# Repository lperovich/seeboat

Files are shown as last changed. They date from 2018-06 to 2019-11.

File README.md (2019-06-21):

# SeeBoat

Laura Perovich (perovich@media.mit.edu, Object-based Media, MIT Media Lab)

This project includes the code, hardware, and fabrication guides for SeeBoat, a community centered waterbody monitoring and data display platform. 

SeeBoat is a fleet of remote controlled boats that measure and display water quality in real time. It allows communities to explore water quality in their local lakes, rivers, and streams by changing the color of the boat in response to changes to the water quality. This data physicalization contextualizes the information and makes the water pollution data present in people's daily lives.

The boats measure water temperature, conductivity, and turbidity and display the data by real-time changes to the colors of the LEDs on the boat. Numeric sensor data is also transmitted via radio, visible through an Android app, and can be further recording using long exposure photos. SeeBoat makes environmental data experiential and interactive to help both communities and researchers better understand pollution and its implications.

The system is based on the Adafruit Feather M0 with RFM95 LoRa Radio (900MHz).

See "hardware" for a parts list, sensor schematics and board files, and 3D print files for sensors attachments.

See "software" for Arduino code for the entire system (main) and for each of the sensors (testing)

See "tutorials" for sensor fabrication guides and testing recommendations.

With technical contributions from Don Blair, Robert Henning, Sophia Struckman, Rod Bayliss, Rima Rebei, and Talia Spitz. Additional testing and assistance by ECO youth group (GreenRoots), Katherine Paseman, Claudia Chen, and Brian Mayton. 

Thanks to contributors Sara Wylie (Northeastern University) and Roseann Bongiovanni (GreenRoots). 

With funding and support from the Object Based Media (V. Michael Bove), the Media Lab Elements Fellows, and the Council for the Arts at MIT.

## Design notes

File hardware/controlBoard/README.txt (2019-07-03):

Laura Perovich: SeeBoat control board for all the sensors 

--third board layer to be used with Featherwing ultimate GPS and Feather M0 LoRa
--see github parts list in hardware folder for parts details

######### Update 7/3/19
Fixed the labels on the LED strand connector

######### Update 6/23/18
Removed on board LED, spaced out the headers to better fit all the parts and the labels
Included DotStar LED strand connector
Water sensor to tell if it's in water is unnecessary, not implemented

######### Update 5/25/17
Combines the fishet-0.1 board with GPS to works as a breakout board for the feather M0 w/LoRa

parts from the fishnet to include:
*tricolor LED (3 pwm pins, other sides to ground)
*on/off switch for board
*temperature sensor connector (SDA, SCL, GND, PWR)
*turbidity sensor connector
*conductivity sensor connector
*water sensor (to tell if it's in water or not) [UNNECESSARY, NOT IMPLEMENTED]

GPS featherwing includes:
*GPS
*clock via GPS

#############################################
ORIGINAL BOARD LAYOUT:
# Adafruit-Ultimate-GPS-FeatherWing-PCB
PCB files for the Adafruit Ultimate GPS FeatherWing
Format is EagleCAD schematic and board layout
For more details, check out the product page at
   * https://www.adafruit.com/products/3133
Designed by Adafruit Industries.  
Creative Commons Attribution, Share-Alike license, check license.txt for more information
All text above must be included in any redistribution

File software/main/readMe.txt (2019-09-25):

SeeBoatRx goes on the feather that's attached to the computer and receiving the data.

SeeBoatFeather goes on the feather that's on the boat. It needs a breakout board with sensor ports plugged into it. In theory it can also have a GPS featherwing plugged in and keep track of GPS location, but in practice this doesn't seem to work (it never gets a fix).

seeBoatGPSdataSD is a workaround for this GPS issue. It can go on an adafruit feather M0 data logging with SD card board that is plugged into an adafruit GPS with featherwing and an extended antenna and can be added to the SeeBoat to seperately log the position of the boat as it is collecting the data. This GPS information saved on the SD card can later be merged with the sensor data saved as a csv on the computer to determine when the boat was at a particular location and create a digital map of the path of the boat and the data. 

The dataToCSV folder contains python sketches for a variety of computers/versions of python. These can be run while SeeBoat is operating and the SeeBoatRx board is connected to the computer. They will display the data coming in as real time plots and at the same time they will save the received data as a csv on the computer. Always run one of these if you want to keep the data. The data is also time stamped. 

The archive folder contains code no longer in use.

Up one level, the testing folder contains sketches that test each part of the system, including each sensor, to make debugging each part individually easier and allow for greater flexibility in putting the systems together.

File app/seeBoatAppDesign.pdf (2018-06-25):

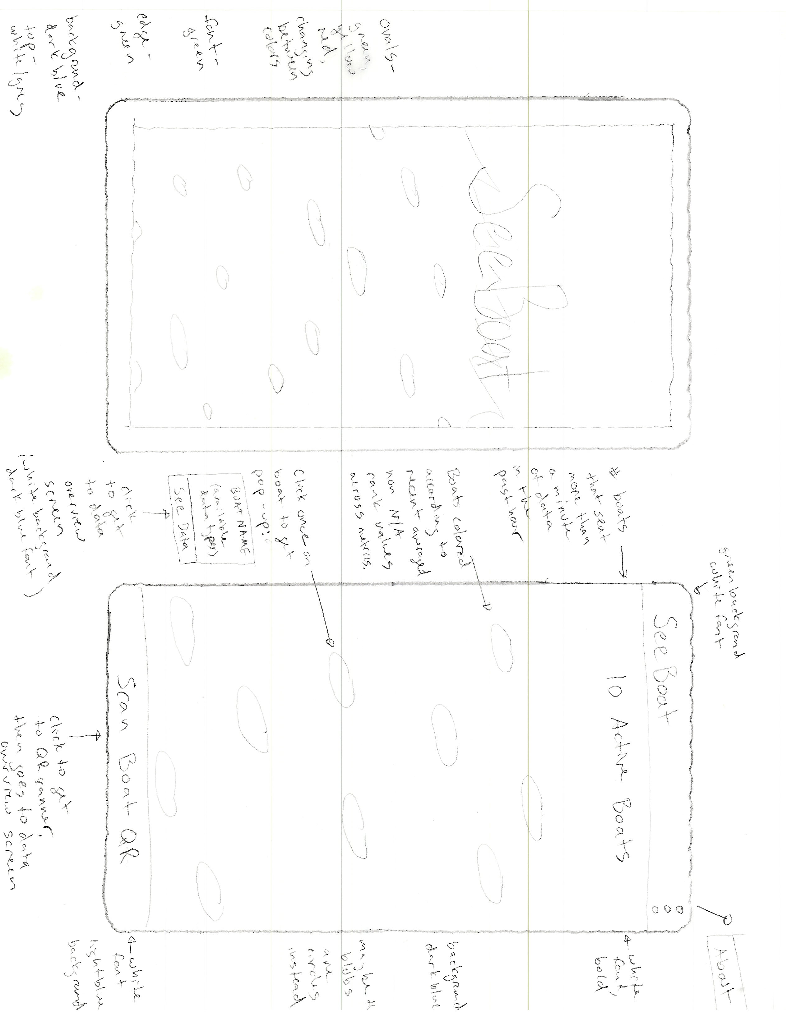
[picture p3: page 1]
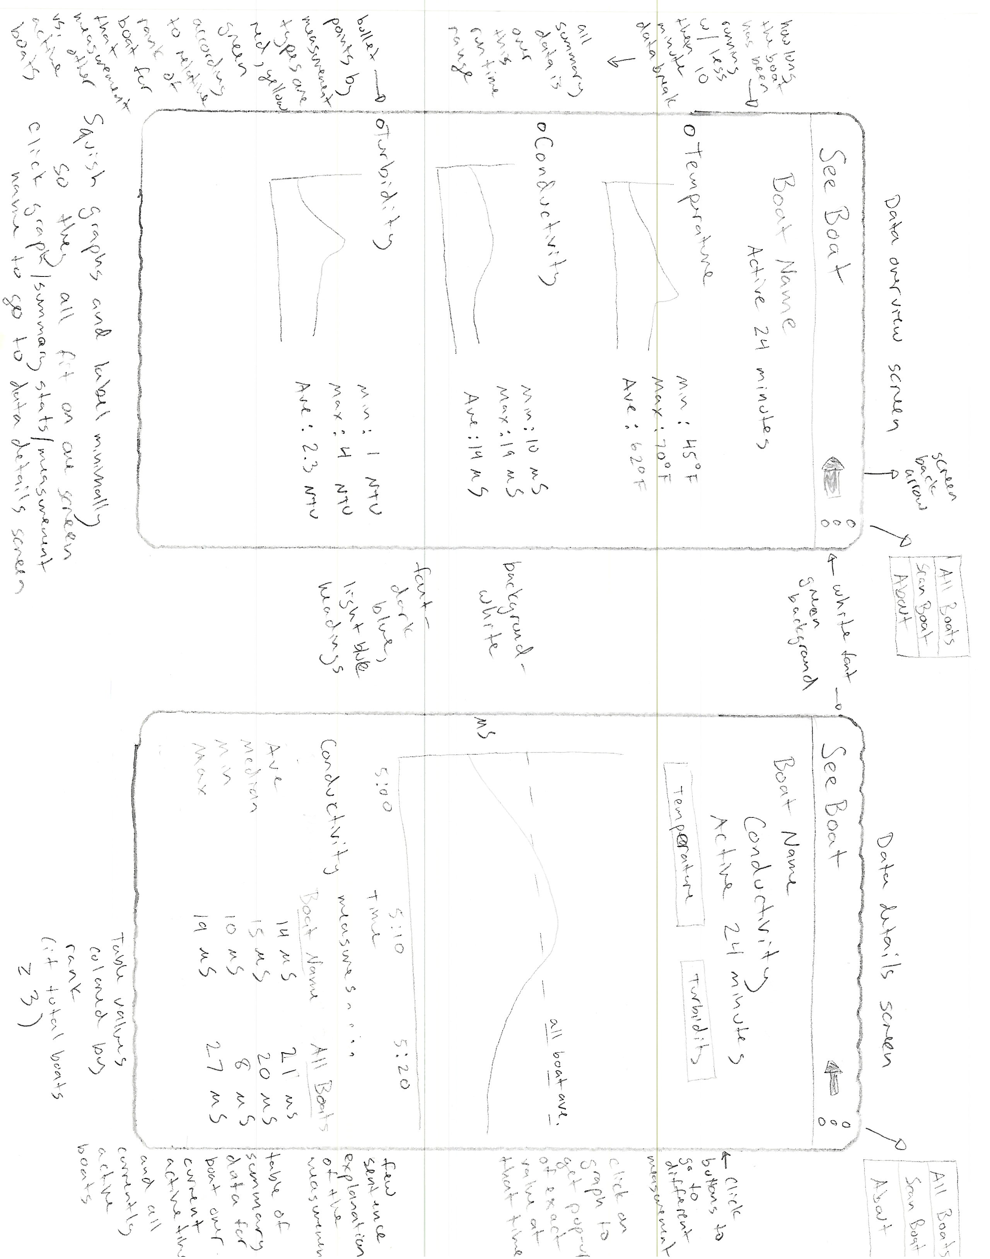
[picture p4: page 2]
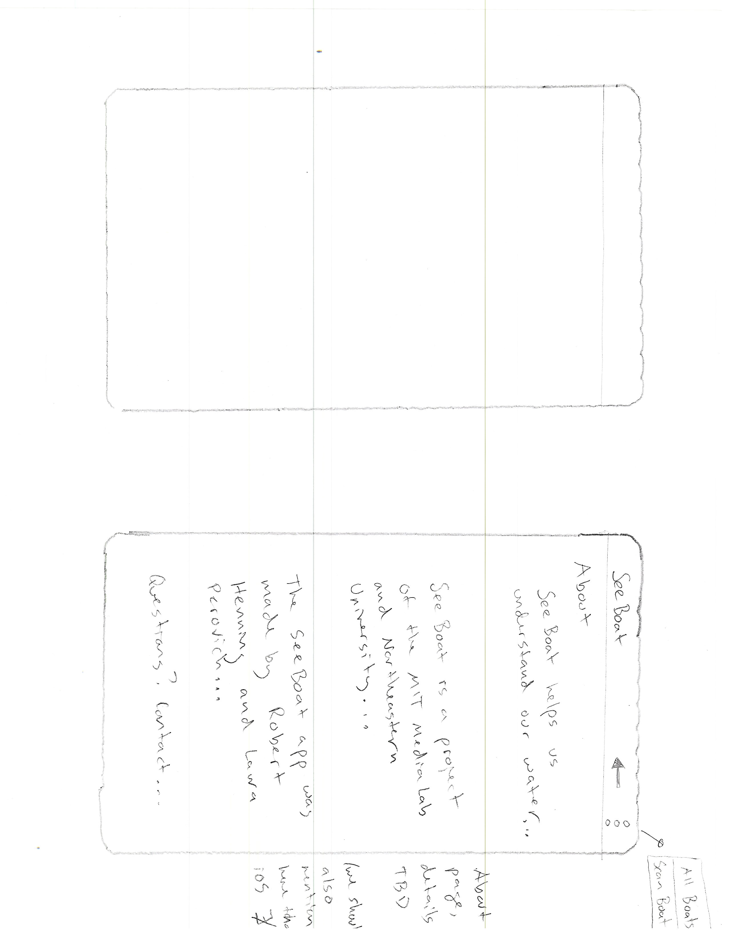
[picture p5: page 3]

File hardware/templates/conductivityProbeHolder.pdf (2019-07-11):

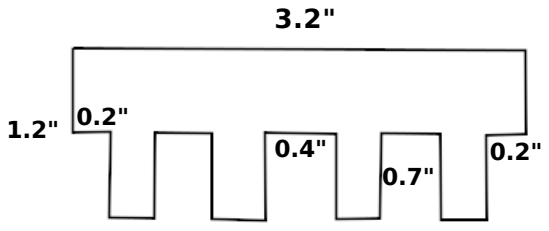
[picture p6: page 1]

1.2"
0.4"
0.7"

0.2"

0.2"

3.2"

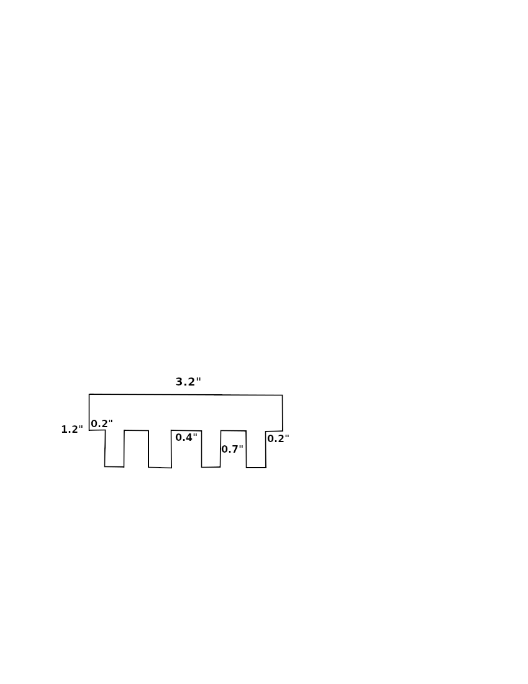
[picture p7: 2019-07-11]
hardware/templates/conductivityProbeHolder.png

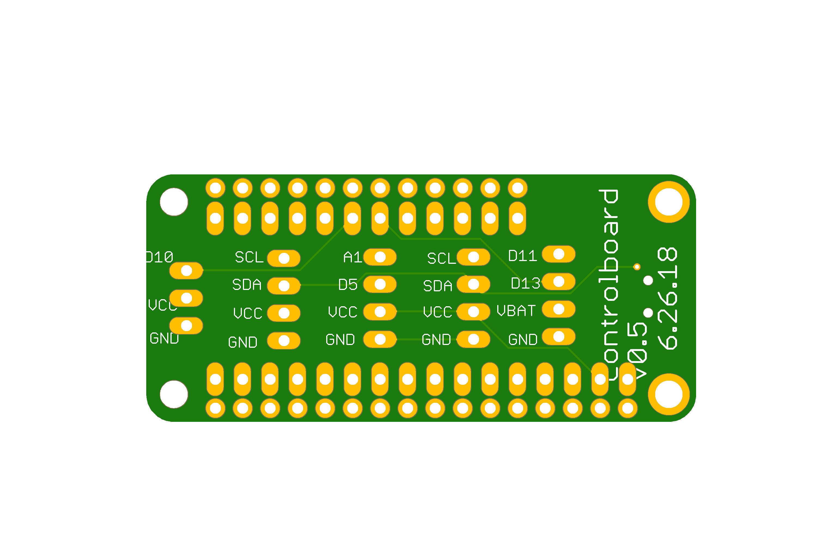
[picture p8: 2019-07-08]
hardware/controlBoard/controlBoard-bottom.png

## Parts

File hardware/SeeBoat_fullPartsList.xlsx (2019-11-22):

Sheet: final
Parts list for SeeBoat & full sensor suite
by Laura Perovich
2018-07-01 | updated June 2019 |  | updated July 2019
BOAT
item |  | part number | place | description | number | cost/item | link
Blackjack 24" Brushless Catamaran RTR |  | PRB08007 | Horizon Hobby | ArtBoat full boat, including radio controller | 1 | $230 | https://www.horizonhobby.com/blackjack-24-inch-catamaran-brushless%3A-rtr-prb08007
LiPo battery Reaction 7.4V 5000mAh 2S 30C LiPo Hardcase: EC3 |  |  | Horizon Hobby | large battery for the boat | 1 | $50 | https://www.horizonhobby.com/74v-5000mah-2s-30c-lipo-hardcase%3A-ec3-dyn9005ec
Krylon K02421007 Fusion for Plastic Spray Paint, Satin Black |  |  | Amazon | to paint the boat so it blends into the background better at night | 1 | $7 | https://www.amazon.com/gp/product/B000C0158E/
isopropyl alcohol |  |  | Amazon | to remove stickers from boat and clean boat | 1 | $8 | https://www.amazon.com/Isopropyl-Alcohol-Solution-16-Ounce/dp/B000P158X8?th=1
AA batteries |  |  | Amazon | for radio controllers | 3 | $15 | https://www.amazon.com/Duracell-MN1500-Duralock-Alkaline-Batteries/dp/B003VSCLMI/
painters tape |  |  | Amazon | to paint the boat so it blends into the background better at night | 1 | $10 | https://www.amazon.com/STIKK-Painters-Release-Finishing-Masking/dp/B01MYP8R5B
600-800 grit sandpaper |  |  | Amazon | to prep the boat for painting | 1 | $7 | https://www.amazon.com/INDUSTRIES-4471-Sandpaper-9-Inch-11-Inch/dp/B001AVYXVU
 |  |  | Amazon
HobbyKing 350w 25A Power Supply (100v~120v) |  |  | Hobby King | liPo battery charger | 1 | $46 | https://hobbyking.com/en_us/hobbyking-350w-25a-power-supply-100v-120v.html
iCharger 208B 350W 8s Balance/Charger |  |  | Hobby King | liPo battery charger | 1 | $126 | https://hobbyking.com/en_us/icharger-206b-300w-8s-balance-charger.html
Stealthwake 23" Brushed Deep-V RTR |  |  | Horizon Hobby | SeeBoat boat, including radio controller, and more space for the sensors than the ArtBoat boat | 1 | $160 | https://www.horizonhobby.com/boats/electric-boats/stealthwake-rtr-23-inch-brushed-deep-v-prb08015
Reaction 7.4V 5000mAh 2S 30C LiPo Hardcase: EC3 |  |  | Horizon Hobby | large battery for the boat, a Ni battery is included with the boat, but this one is better for longer use | 1 | $50 | https://www.horizonhobby.com/74v-5000mah-2s-30c-lipo-hardcase%3A-ec3-dyn9005ec
CONTROL BOARD
item |  | part number | place | description | number | cost/item | link
Adafruit feather M0 LoRa RMF95 900MHz |  |  | Adafruit | main radio board | 1 | $35 | https://www.adafruit.com/product/3178
Adafruit ultimate GPS featherwing |  |  | Adafruit | GPS breakout | 1 | $40 | https://www.adafruit.com/product/3133
lithium coin cell battery |  |  | Adafruit | for GPS featherwing | 1 | $1 | https://www.adafruit.com/product/380
male headers |  |  | Adafruit | for top board | 1 | $3.00 | https://www.adafruit.com/product/392
feather stacking long female headers |  |  | Adafruit | for middle board | 4 | $1.25 | https://www.adafruit.com/product/2830
feather female headers |  |  | Adafruit | for bottom board | 4 | $1.00 | https://www.adafruit.com/product/2886
micro USB cable |  |  | Amazon | cable for programming feather | 1 | $5.59 | https://www.amazon.com/gp/product/B00NH13O7K
liPo battery 2500mAh mAh 3.7V |  |  | Adafruit | substantial enough to work with LED strip (https://learn.adafruit.com/lightship-led-animation-over-wifi/hardware circuit 1) | 1 | $15 | https://www.adafruit.com/product/328
custom breakout board |  |  | OSH Park | connects to all sensors | 1 | $5 | https://github.com/lperovich/seeboat/tree/master/hardware/controlBoard
resistor SMD 0603 2.7K |  | RNCP0603FTD2K74CT-ND | Digikey | for I2C--exact value is important!! | 2 | $0.10 | https://www.digikey.com/products/en?keywords=RNCP0603FTD2K74CT-ND
resistor SMD 0603 100 ohm |  | RNCP0603FTD100RCT-ND | Digikey | for the optional on-board LED | 3 | $0.10 | https://www.digikey.com/product-detail/en/stackpole-electronics-inc/RNCP0603FTD100R/RNCP0603FTD100RCT-ND/2240425
DPDT switch SMD |  | 401-2013-1-ND | Digikey | turns the board on/off | 1 | $1.07 | https://www.digikey.com/product-detail/en/AYZ0202AGRLC/401-2013-1-ND/1640122
optional SMD LED, dotstar 5050 |  | 2343 | Adafruit | can be used for testing on board, same LED as in strip | 1 | $4.50 | https://www.adafruit.com/product/2343
4-pin header female Molex, LLC 0705430003 |  | WM4802-ND | Digikey | connects out to sensors (female, on board) | 4 | $0.94 | https://www.digikey.com/products/en?keywords=WM4802-ND
4-pin header male Molex Connector Corporation 0014562042 |  | WM9131-ND | Digikey | connects out to sensors (male, on wire) | 4 | $1.46 | https://www.digikey.com/products/en?keywords=WM9131-ND
3-pin header female Molex, LLC 0705430002 |  | WM4801-ND | Digikey | connects out the turbidity sensor (female, on board) | 1 | $0.87 | https://www.digikey.com/products/en?keywords=WM4801-ND
3-pin header male Molex Connector Corporation 14-56-2032 |  | WM10647-ND | Digikey | connects out the turbidity sensor (male, on wire) | 1 | $0.99 | https://www.digikey.com/products/en?keywords=WM10647-ND
flat ribbon cable 3M 3302/16 300SF |  | MC16M-100-ND | Digikey | connects out to sensors and lights | 1 | $95.15 | https://www.digikey.com/product-detail/en/3m/3302-16-300SF/MC16M-100-ND/145737 | verify this is the right answer
wire-white single strand | 22 AWG | C2004W-100-ND | Digikey | for short antenna for LoRA radio | 1 | $16 | https://www.digikey.com/product-detail/en/general-cable-carol-brand/C2004A.12.02/C2004W-100-ND/57495
LIGHTS
item |  | part number | place | description | number | cost/item | link
Adafruit DotStar Digital LED Strip - White 60 LED - Per Meter - WHITE |  |  | Adafruit | 5V plays nice with the feather | 1 | $30 | https://www.adafruit.com/product/2240
silicon clear adhesive for water applications |  |  | Tag Hardware | to glue acrylic strips to boat | 1 | $8.00
1/8" satin ice white acrylic strips (~2"x17" per strip, purchase strips as a block) |  |  | Tap Plastics | testing using acrylic (with epoxy casting?) to display lights through holes cut into the boat to replace the dragonskin silcon encased LED strip on the outside of the boat | 1 | $10 | https://www.tapplastics.com/product/plastics/cut_to_size_plastic/satinice_white/655
pH SENSOR
item |  | part number | place | description | number | cost/item | link
Atlas Scientific EZO pH Circuit Part # EZO-pH |  |  | Atlas Scientific | 3.3V plays nice with the feather | 1 | $38 | https://www.atlas-scientific.com/product_pages/circuits/ezo_ph.html
Atlas Scientific ph probe Part # ENV-40-pH |  |  | Atlas Scientific | 3.3V plays nice with the feather | 1 | $72 | https://www.atlas-scientific.com/product_pages/probes/ph_probe.html
Electrically Isolated EZO™ Carrier Board |  |  | Atlas Scientific | 3.3V plays nice with feather | 1 | $40 | https://www.atlas-scientific.com/product_pages/components/single_carrier_iso.html
pH standards; 4, 7, and 10 |  |  | Hach | to calibrate the probe | 1 | $30 | https://www.hach.com/ph-buffer-solution-kit-color-coded-ph-4-01-ph-7-00-and-ph-10-01-500-ml-each/product?id=7640205069
KCl solution |  |  | Hach | for storing the probe in while it's not in use | 1 | $12 | https://www.hach.com/electrolyte-solution-kcl-3m-50ml/product-parameter-reagent?id=7640207762
3/4” 8-32 screws |  |  | Ace Hardware | to attach the holder to the boat | 2 | $0.15
8-32 nuts |  |  | Ace Hardware | to attach the holder to the boat | 2 | $0.08
5/32 rubber washers |  |  | Ace Hardware | to attach the holder to the boat and water seal | 4 | $0.14
Plastic Expansion Routing Clamp, 5/8" ID, 2-7/16" Long |  |  | McMaster Carr | holder to attach the probe to the boat | 1 | $0.55 | https://www.mcmaster.com/8972T11
1/2” inner diameter foam tubing, ~1” length |  |  | McMaster Carr | foam tubing to go around the probe so it securely attaches in the holder | 1 | $0.9 | https://www.mcmaster.com/4339T5
small rubber band/o-ring |  |  |  | to make the foam tubing secure on the pH probe | 1 | $0.14
5/16" inner diameter o-ring, 1/16" thick |  |  |  |  | 2 |  | pill hardware on mass ave
6/16" inner diameter o-ring, 1/8" thick |  |  |  |  | 2 |  | pill hardware on mass ave
foam tape
CONDUCTIVITY SENSOR
item |  | part number | place | description | number | cost/item | link
custom conductivity board |  |  | OSH Park |  | 1 | $7 | https://github.com/lperovich/seeboat/tree/master/hardware/conductivity
resistor 10K, 0603 |  | YAG2122CT-ND | Digikey |  | 4 | $0.17 | https://www.digikey.com/product-detail/en/yageo/AT0603FRE0710KL/YAG2122CT-ND/5139570
resistor, 2.7K, 0603 |  | RNCP0603FTD2K74CT-ND | Digikey |  | 1 | $0.10 | https://www.digikey.com/product-detail/en/stackpole-electronics-inc/RNCP0603FTD2K74/RNCP0603FTD2K74CT-ND/2240457
resistor, 1M, 0603 |  | YAG4498CT-ND | Digikey |  | 1 | $0.34 | https://www.digikey.com/product-detail/en/yageo/RT0603BRD071ML/YAG4498CT-ND/6616654
resistor, 1K, 0603 |  | RNCP0603FTD1K00CT-ND | Digikey |  | 2 | $0.10 | https://www.digikey.com/product-detail/en/stackpole-electronics-inc/RNCP0603FTD1K00/RNCP0603FTD1K00CT-ND/2240445
resistor, 42K, 0603 |  | YAG4556CT-ND | Digikey |  | 1 | $0.34 | https://www.digikey.com/product-detail/en/yageo/RT0603BRD0742K2L/YAG4556CT-ND/6616712
resistor, 1.2K, 0603 |  | 311-2461-1-ND | Digikey |  | 1 | $0.12 | https://www.digikey.com/product-detail/en/yageo/RT0603DRE071K2L/311-2461-1-ND/6128880
capacitor, 0.1 uF, 0603 |  | C1608X8R1H104K080AB | Digikey |  | 1 | $0.32 | https://www.digikey.com/product-detail/en/tdk-corporation/C1608X8R1H104K080AB/445-8818-1-ND/3248223
diode |  | 641-1331-1-ND | Digikey |  | 2 | $0.37 | https://www.digikey.com/products/en?keywords=641-1331-1-ND
rail splitter |  | TLE2426CLPR | Digikey |  | 1 | $1.86 | https://www.digikey.com/product-detail/en/texas-instruments/TLE2426CD/296-6547-5-ND/371934
op-amp |  | JFET, AD8655ARZ-REEL7CT-ND | Digikey |  | 1 | $2.64 | https://www.digikey.com/product-detail/en/analog-devices-inc/AD8655ARZ-REEL7/AD8655ARZ-REEL7CT-ND/3678589
op-amp |  | TLV2374 (TLV2374IDR) |  |  | 1 | $1.81 | https://www.digikey.com/product-detail/en/texas-instruments/TLV2374IDR/296-11967-1-ND/390435
DPDT switch SMD |  | 401-2013-1-ND | Digikey | switches between the two resistor values (high or low conductivity ranges) | 1 | $1.07 | https://www.digikey.com/product-detail/en/AYZ0202AGRLC/401-2013-1-ND/1640122
wire-green single strand | 22 AWG | C2117G-100-ND | Digikey | to connect the board to screws in probe | 1 | $16 | https://www.digikey.com/product-detail/en/general-cable-carol-brand/C2117A.12.06/C2117G-100-ND/16217
wire-white single strand | 22 AWG | C2004W-100-ND | Digikey | to connect the board to screws in probe | 1 | $16 | https://www.digikey.com/product-detail/en/general-cable-carol-brand/C2004A.12.02/C2004W-100-ND/57495
Molex 2 pin header (female) |  | WM4800-ND | Digikey | to connect the probe wires to the board | 1 | $0.84 | https://www.digikey.com/products/en?keywords=%09WM4800-ND
Molex 2 pin header (male) |  | WM24819-ND | Digikey | to connect the probe wires to the board | 1 | $0.78 | https://www.digikey.com/products/en?keywords=WM24819-ND
3D printed probe |  |  | Eden Vero White | sensor probe | 1
foam tubing: Multipurpose Blended Neoprene Foam Tube, 1" OD, 3/4" ID, 10 Feet Long |  |  | McMaster Carr | connects to the boat directly to hold the conductivity probe in place | 1 | $9.21 | https://www.mcmaster.com/2029n13
plastic to plastic epoxy |  |  | Amazon | to glue the foam tubing to the boat, also used for the turbidity holder and the LED panels | 1 | $7.12 | https://www.amazon.com/gp/product/B01IBOK7FE/
Screws, 6-32 1/2” |  |  |  | for within the probe, water contact | 2
nuts |  |  |  | for within the probe, water contact | 2
black epoxy |  | see turbidity sensor | see turbidity sensor | for waterproofing the screws in the probe | see turbidity sensor | see turbidity sensor | see turbidity sensor
Conductivity 2-point Calibration Standard 2-Pack 8oz each 700 uS and 2000 uS |  |  | Amazon | to calibrate the probe | 1 | $17 | https://www.amazon.com/gp/product/B01F2R2EPE/
Conductivity 2-point Calibration Standard 2-Pack 8oz each 100 uS and 3000 uS |  |  | Amazon | to calibrate the probe | 1 | $17 | https://www.amazon.com/gp/product/B01F7L9QD8/
TURBIDITY SENSOR
item |  | part number | place | description | number | cost/item | link
Infrared Diode ("LED") |  | VSMY2850G | Digikey |  | 1 | $1.06 | https://www.digikey.com/product-detail/en/vishay-semiconductor-opto-division/VSMY2850G/VSMY2850GCT-ND/2615293
Light-to-Frequency Sensor |  | TSL237T | Digikey |  | 1 | $5.31 | https://www.digikey.com/product-detail/en/ams/TSL237T/TSL237-TCT-ND/3095287
0.1 µF capacitor |  | C1608X8R1H104K080AB | Digikey |  | 1 | $0.32 | https://www.digikey.com/product-detail/en/tdk-corporation/C1608X8R1H104K080AB/445-8818-1-ND/3248223
200 ohm resistor |  | Yageo RT0603DRD07200RL | Digikey |  | 1 | $0.12 | https://www.digikey.com/product-detail/en/yageo/RT0603DRD07200RL/311-200DCT-ND/1035740
custom light to freq board |  |  | OSH Park |  | 1 | $3 | https://github.com/lperovich/seeboat/tree/master/hardware/turbiditySensor
custom LED board |  |  | OSH Park |  | 1 | $3 | https://github.com/lperovich/seeboat/tree/master/hardware/turbidityLED
wire-black, stranded | 20-22 AWG |  | Digikey | to connect the boards to each other | 1 | $25 | https://www.digikey.com/product-detail/en/alpha-wire/422010-BK005/422010-BK005-ND/3705786
wire-red, stranded | 20-22 AWG |  | Digikey | to connect the boards to each other | 1 | $25 | https://www.digikey.com/product-detail/en/alpha-wire/422010-RD005/422010-RD005-ND/4935160
wire-grey stranded | 20-22 AWG |  | Digikey | to connect the boards to each other | 1 | $25 | https://www.digikey.com/product-detail/en/alpha-wire/422010-SL005/422010-SL005-ND/4935161
~1/8" acrylic black, roughly 2"x5" |  |  | Amazon | to mount senor & LED at right angles; also to "focus" the LED light | 1 | $13 | https://www.amazon.com/Source-One-LLC-Acrylic-Plexiglass/dp/B06XNXHKQN/
black thermally conductive epoxy |  |  | Amazon | for waterproofing the electronics, as with temperature sensor | 1 | $43.95 | https://www.amazon.com/MG-Chemicals-Thermally-Conductive-Encapsulating/dp/B008UH4CRM
cutting oil; soluble oil |  |  | Amazon | to calibrate the turbidity sensor | 1 | $15 | https://www.amazon.com/CRC-SL2512-Soluble-Oil-32/dp/B000M8O010/
small glass viles |  |  | Discount Vials | to calibrate the turbidity sensor | 1 | $17 | https://www.discountvials.com/6-dram-glass-vial-w-cap/
Hach turbidity standard, 500 mL (Wijnen) |  |  | Hach | THIS IS SUPER TOXIC; to calibrate the turbidity sensor | 1 | $80 | http://www.hach.com/formazin-turbidity-standard-4000-ntu-500-ml/product?id=7640455437
TEMPERATURE SENSOR
item |  | part number | place | description | number | cost/item | link
custom temp board |  |  | OSH Park | custom temperature board | 1 | $5 | https://github.com/lperovich/seeboat/tree/master/hardware/temperatureSensor
digital temperature sensor |  | AT30TS750A-SS8M-T | Digikey | temperature sensor | 1 | $0.60 | https://www.digikey.com/product-detail/en/microchip-technology/AT30TS750A-SS8M-T/1611-AT30TS750A-SS8M-TCT-ND/6831450
resistor, 10K, 1206 |  | RC1206FR-0710KL | Digikey | check this value | 1 | $0.10 | http://www.digikey.com/product-detail/en/RC1206FR-0710KL/311-10.0KFRCT-ND/731430
capacitor, 0.1 uF, 1206 |  | 478-5724-1-ND | Digikey |  | 1 | $0.36 | https://www.digikey.com/product-detail/en/avx-corporation/1206VC104KAT2A/478-5724-1-ND/2136332
flat ribbon cable 3M 3302/16 300SF |  | see control board | see control board | board to control board connector | see control board | see control board | see control board
black epoxy |  | see turbidity sensor | see turbidity sensor | for waterproofing the electronics | see turbidity sensor | see turbidity sensor | see turbidity sensor

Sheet: scrap
BOAT AESTHETICS
LED strip trying to get it more diffuse but still bright enough |  |  |  |  | The plastic appears similar to the translucent or 'opal' acrylic sold for signs and lightboxes. The back face is covered with an adhesive aluminum foil reflector. Aluminum foil tape is available at most hardware stores.
trying to get this effect: https://www.adafruit.com/product/1621
opal acrylic
acrylic and more |  | https://www.piedmontplastics.com/applications/light-boxes | reached out to them via online form 6/6/18 | they will send me some samples, suggested #7328 white
diffuser acrylic sheets |  | http://www.chinaacrylicsheet.com/ | reached out to them via online form 6/6/18 about their backlit diffuser things
more acrylic options |  | https://www.tapplastics.com/ | reached out to them via online form 6/6/18 about their backlit diffuser things | suggested satin ice white--ordered a sample | https://www.tapplastics.com/product/plastics/cut_to_size_plastic/satinice_white/655
more plastics options |  | http://www.eplastics.com/ | reached out to them via email 6/6/18 | suggested this one: http://www.eplastics.com/Plastic/lighting-diffusers/lumen-xt-lw3-polycarbonate-sheet asked for sample
more lightbox focus |  | https://www.lightboxes.com/ | reached out to them via online form 6/6/18 | they suggested an option, I asked if I could get a sample of it 6/8/18 | they wanted to charge $30 to ship the sample, so no go
 |  | http://www.plasticsheets.com/opal-acrylic-sheet/ | has the right material, but UK site
 |  | https://www.cutplasticsheeting.co.uk/frosted-acrylic-perspex-sheeting/opal-frost-acrylic-sheeting | another UK site
 |  | https://www.simplyplastics.com/catalog/products-by-use/plastic-lighting-materials/opal-acrylic-light-diffusing-sheet/c-24/c-110/p-667 | more UK sites
 |  | https://www.cloudynights.com/topic/496450-looking-for-opaque-plastic-for-light-box/ | useful thread!!!
 |  |  | translucent white acrylic from McMaster plus sanding
 |  |  | ask local industrial plastics supplier
acrylic sheets |  | http://www.estreetplastics.com/SearchResults.asp?Search=1%2F8%22+2447&Search.x=0&Search.y=0 | 1/8" 2447 White Translucent Sheet | emailed them about this product
Paint or stickers for boat??
SCRAP
wire-red single strand | 22 AWG |  |  | 1 | 16 | https://www.digikey.com/product-detail/en/general-cable-carol-brand/C2004A.12.03/C2004R-100-ND/53789
wire-black single strand | 22 AWG |  |  | 1 | 16 | https://www.digikey.com/product-detail/en/general-cable-carol-brand/C2004A.12.01/C2004B-100-ND/57431
short male headers |  | Adafruit | for top board | 4 | $0.50 | https://www.adafruit.com/product/3002
short female headers |  | Adafruit |  | 4 | $1.50 | https://www.adafruit.com/product/2940
dragon skin 30 |  | Amazon | for opaque LED strip | 1 | $31 | https://www.amazon.com/dp/B00EOA0EC6/ref=cm_sw_r_cp_api_xzDjAbNHV1FRW
powdered sugar |  | grocery store | to make the LEDs diffuse more through the silicon | 1 | $8 | https://www.amazon.com/Domino-Powdered-Confectioners-Sugar-16oz/dp/B0019N2EQU
waterproof adhesive |  | Amazon | for sealing the holes the LED wires go through and attaching LEDs to boat; other options could work | 1 | $27 | https://www.amazon.com/gp/product/B000H83M4G/
acrylic (1/8", 12"x24") |  | Amazon | for making a box to use for casting the LEDs in silicon | 1 | $25 | https://www.amazon.com/Source-One-LLC-Acrylic-Plexiglass/dp/B01FEF0VQI/
white polyester transparent fabric |  | local fabric store | to put in silicon to diffuse the LED strip more | 1 | $5
aluminum tape for reflecting |  | Amazon | backing for LED strip to maximize light out--test this | 1 | $10 | https://www.amazon.com/Aluminum-Tape-Foil-Ducts-Insulation/dp/B01FROBUXE/

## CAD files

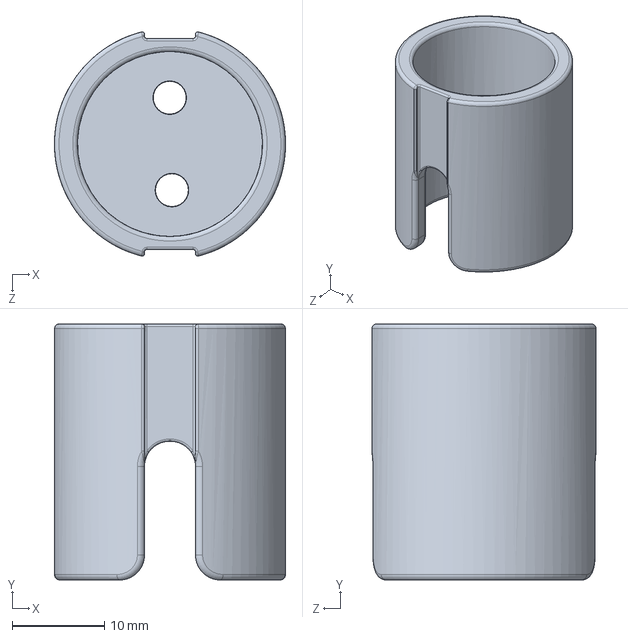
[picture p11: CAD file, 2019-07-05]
hardware/3Dprint/conductivityProbe.SLDPRT
25.0 x 27.7 x 24.2 mm

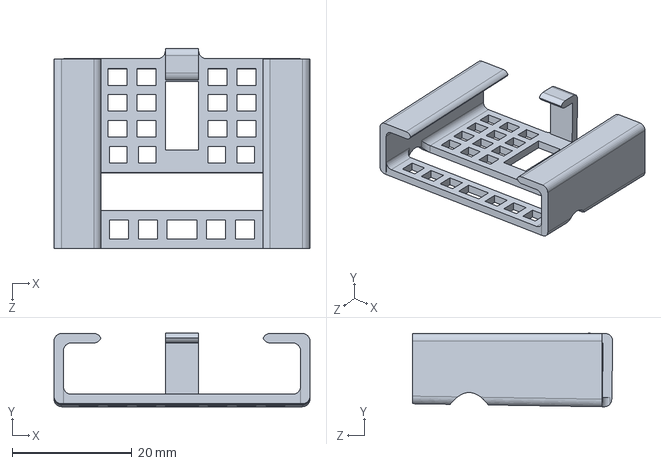
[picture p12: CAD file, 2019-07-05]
hardware/3Dprint/turbidityBoatAttachment.sldprt
42.8 x 12.3 x 33.5 mm

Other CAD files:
hardware/3Dprint/conductivityProbe.DXF
hardware/3Dprint/conductivityProbe.STL
hardware/3Dprint/turbidityBoatAttachment.DXF
hardware/3Dprint/turbidityBoatAttachment.STL

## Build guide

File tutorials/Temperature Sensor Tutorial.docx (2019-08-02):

# Temperature Sensor Tutorial/troubleshooting

Talia Spitz Spring 2019

# Probe

The probe for the temperature sensor is covered in epoxy in order to waterproof it. It is the only part of the sensor which should be immersed in water.

## Manufacturing

### Parts list for the probe:

Part | Amount | Notes | Image

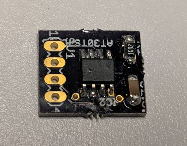
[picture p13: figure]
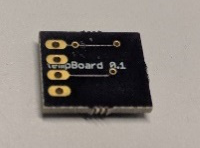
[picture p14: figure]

Custom temp board | 1 | you can find the board schematic at: https://www.dropbox.com/sh/mgy3ndqnzldy1xk/AABXH-txk6h3GChvCx_p5i7ma?dl=0

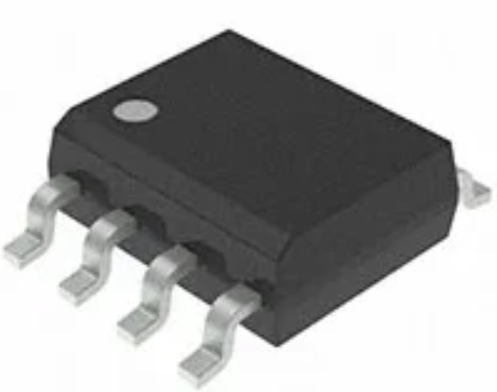
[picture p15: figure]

Digital temp sensor | 1 | Part number: AT30TS750A-SS8M-T, Digikey
10 kΩ resistor, 1206 | 1 | Part number: RC1206FR-0710KL, Digikey
0.1 µF capacitor, 1206 | 1 | Part number: 478-5724-1-ND or 399-4674-1-ND, Digikey

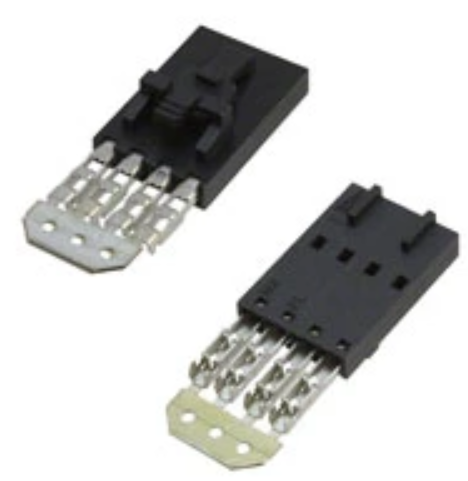
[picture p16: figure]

4-pin header | 1 | Part number: WM9131-ND, Digikey
Wire | 4 (different colors) | By convention, we use black, white, grey, and purple ribbon wire.

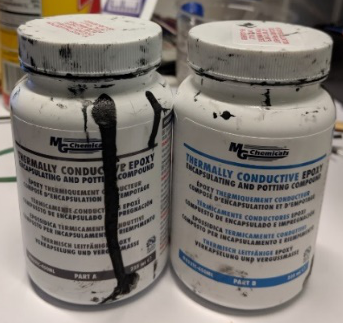
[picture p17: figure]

MG Chemicals epoxy | 1 | Part number: 832TC-450ML https://www.amazon.com/MG-Chemicals-Thermally-Conductive-Encapsulating/dp/B008UH4CRM#product-description-iframe

### Steps:

1) Firstly, you’ll want to attach the wires to the connector. Cut the ribbon wire to about 1 foot in length. Crimp them in place by hand first, then solder them in. When you’re done, carefully push them into the plastic case, and snap off the metal tag. It’s easy to break the wires while you’re doing this, so be gentle. If it’s needed, you can carefully use a pair of pliers to push the wires in.

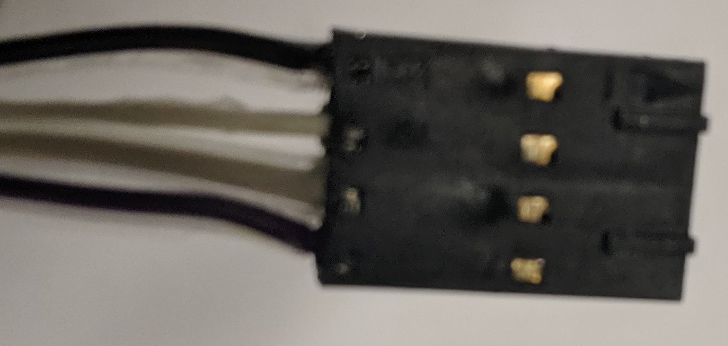
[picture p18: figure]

The finished connection.

2) Follow the board schematic and solder on the resistor, capacitor, and temperature sensor.

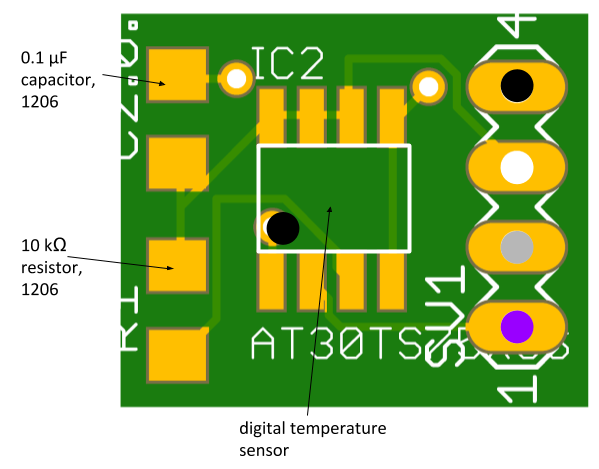
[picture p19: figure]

Annotated temperature circuit board schematic.

3) Solder the wires to their corresponding pins.
4) **Test to see if the sensor works before epoxying it!!** Follow the directions on the epoxy containers to waterproof the probe. The epoxy should cover the whole circuit board and up the wires a little bit.

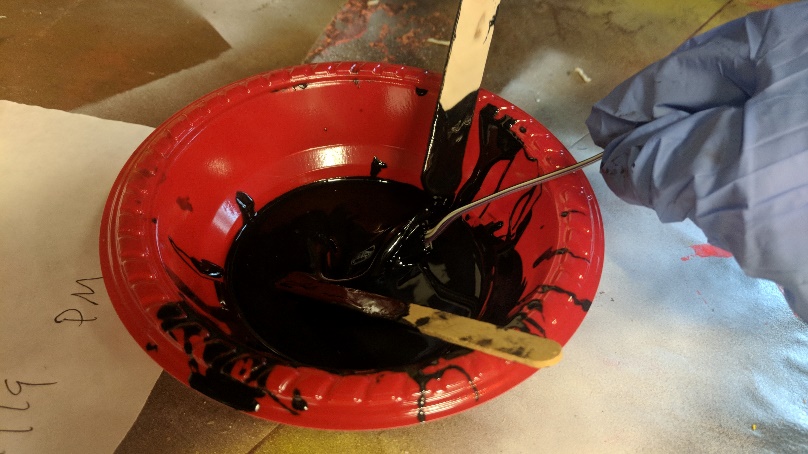
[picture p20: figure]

First dip the board into the epoxy, then use a popsicle stick to spread the epoxy up the wires and make sure the entire board is coated. Once you’re sure it’s covered, gently scrape off excess epoxy so it doesn’t drip while it cures.

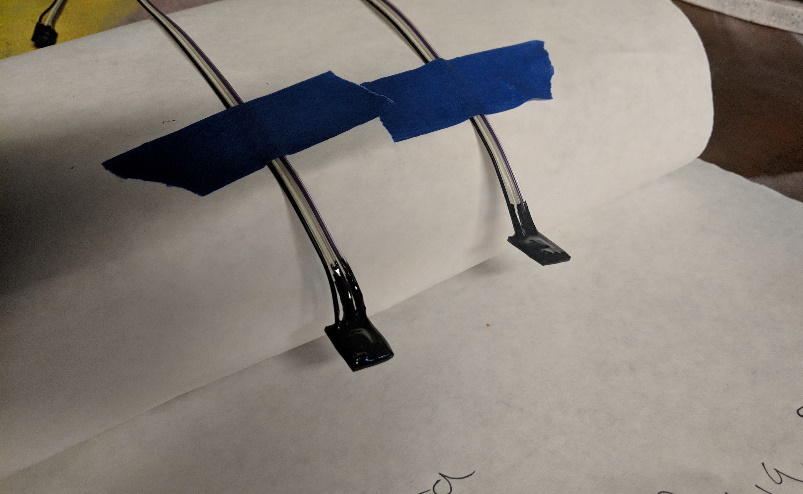
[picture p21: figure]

Leave the epoxied sensors to cure for 24 hours. Check them after a couple of hours to see if you need to touch up any areas with more epoxy, or if you need to scrape off any more excess.

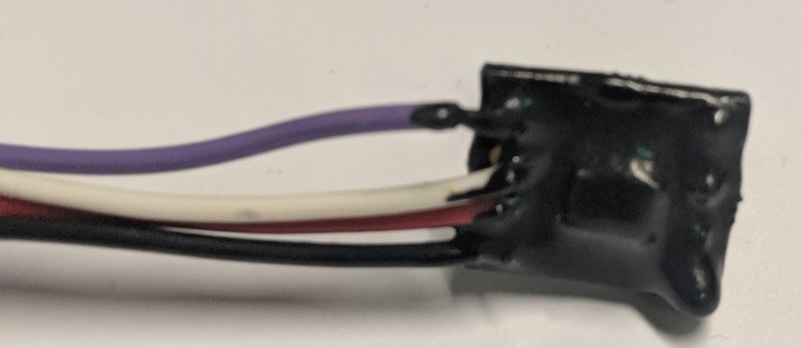
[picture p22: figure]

The cured epoxy (black) should look like this.

# troubleshooting

To test if your temperature sensor is working, plug it into the Feather, and run the ‘tempWire’ (found at: “GitHub\seeboat\software\testing\temperature\tempWire\tempWire.ino”) file in Arduino. The serial monitor should print the temperature reading in both Celsius and Fahrenheit.

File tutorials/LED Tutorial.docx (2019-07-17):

# LED tutorial

# Manufacturing

### Parts list:

Part | Amount | Notes | Image

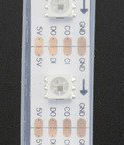
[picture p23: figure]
Adafruit DotStar Digital LED Strip - White 60 LED - Per Meter - WHITE

Adafruit DotStar Digital LED strip | 1 | https://www.adafruit.com/product/2240?length=1

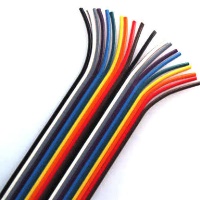
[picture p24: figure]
Image result for ribbon wire

Ribbon wire | ~3 ft | We used black, grey, white, and purple wires.

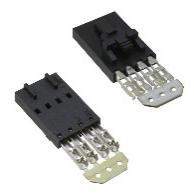
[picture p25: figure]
Image result for WM9131-ND

4-pin header | 1 | Part number: WM9131-ND

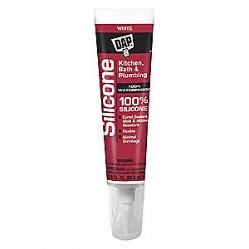
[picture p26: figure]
White Sealant, Silicone, 2.8 oz.

Silicone glue | 1 | https://www.grainger.com/product/406W20?gclid=CjwKCAjwvJvpBRAtEiwAjLuRPZ_Sl7sjaj8k1NH8XQdIhp3zyGGysJu4nPp_T-i7-aUdAsLFmiFH5xoCrLIQAvD_BwE&cm_mmc=PPC:+Google+PLA&ef_id=CjwKCAjwvJvpBRAtEiwAjLuRPZ_Sl7sjaj8k1NH8XQdIhp3zyGGysJu4nPp_T-i7-aUdAsLFmiFH5xoCrLIQAvD_BwE:G:s&s_kwcid=AL!2966!3!281733020561!!!g!427397951721! (https://www.grainger.com/product/406W20?cm_mmc=PPC:+Google+PLA&s_kwcid=AL!2966!3!281733020561!!!g!427397951721!)

### Steps:

1) Measure and cut the LED strand and ribbon wire to the correct lengths based on the drawing below. Every time you cut the strand, you’ll lose one LED, so be careful when measuring.

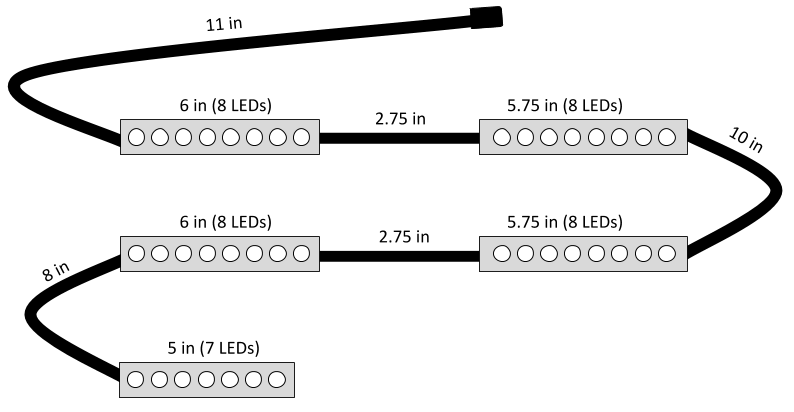
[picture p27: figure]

These are the measurements we used to make the LED strand one continuous piece. The black lines represent the ribbon wire. The 6 in LED strips are for the back side panels, the 5.75 in strips are for the front side panels, and the 5 in strip is for the top panel.

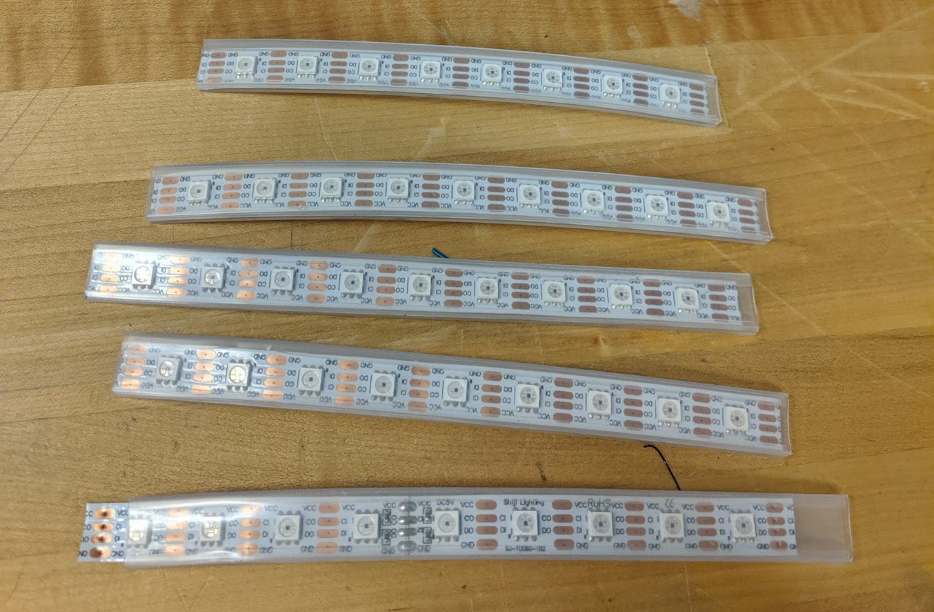
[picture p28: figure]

This is what the strands should look like after they’ve been cut.

2) Use a tack or other wire to make the holes in the LED strip larger so it will be easier to solder.

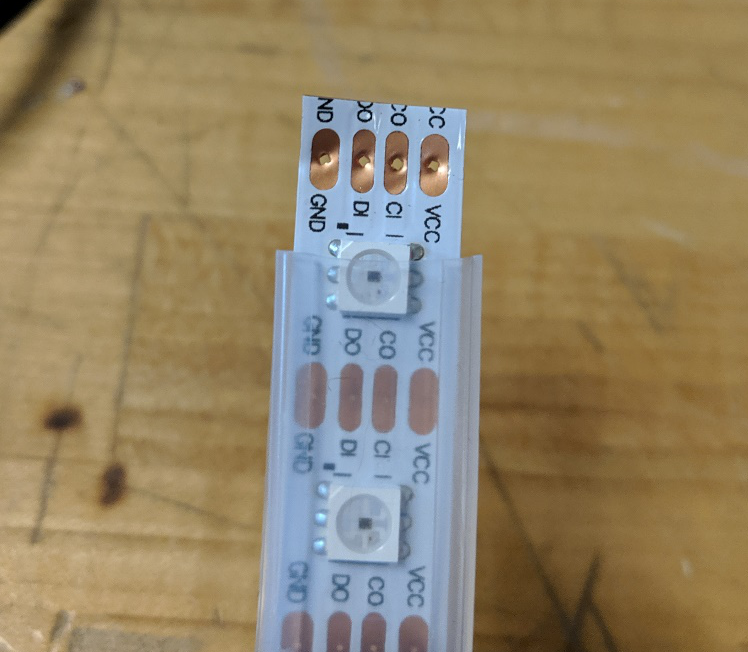
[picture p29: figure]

The top holes were enlarged by poking a wire through them.

3) Strip the ribbon wire, and insert the wires into the holes on the LED strip, and bend them so they stay still while you’re soldering. Try to follow the convention of black wire → GND. Also make sure to trim any free wire after you’re finished soldering.

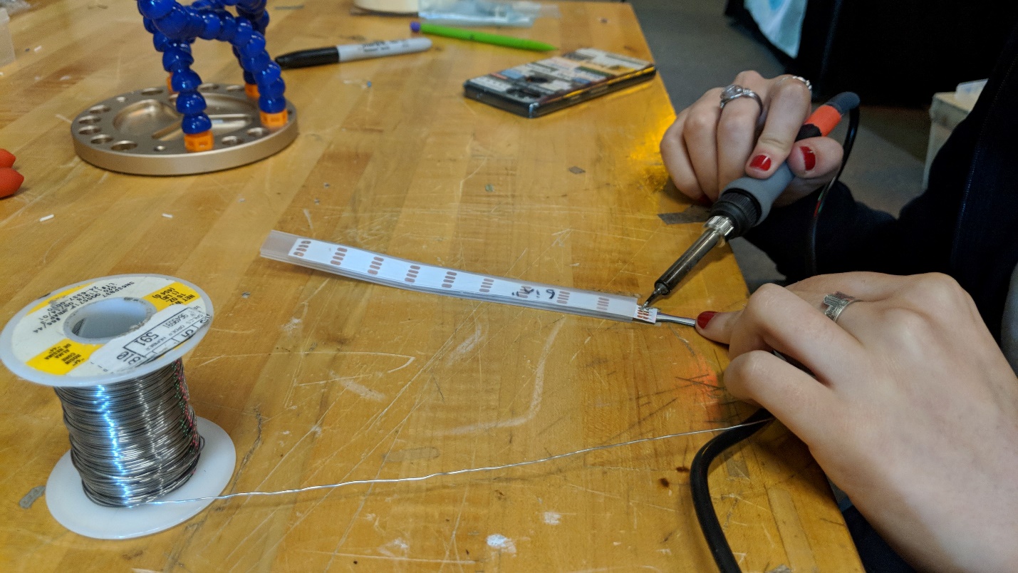
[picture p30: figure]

The wires are threaded through the top of the holes, then bent at the back so it’s easier to solder on the bottom. You can also solder on the top if wire is exposed.

4) Once everything is soldered together, double check that you’ve wired it correctly! If you accidentally switch VCC and GND, you can burn out the LEDs.
5) Test the strip!
6) After you’ve tested the strip, use silicone glue and seal the ends to make it watertight.

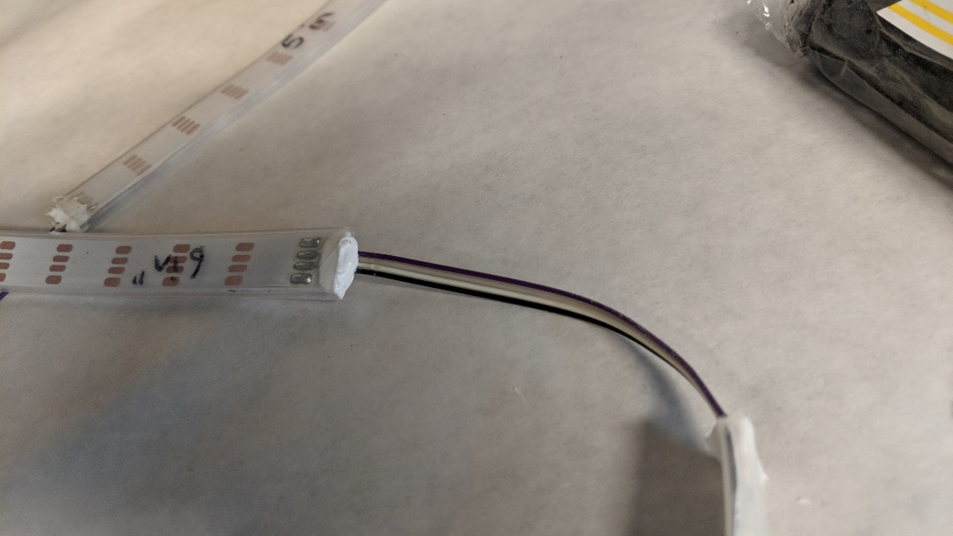
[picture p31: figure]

A sealed LED strip.

# Testing

Use the tester code which can be found at: “GitHub\seeboat\software\testing\LED." The LEDs should cycle through colors all the way down to the end of the strand. If it’s not working, add more solder, and make sure a battery is plugged into the Feather, as sometimes the LEDs are fussy and only work when you plug in a battery.

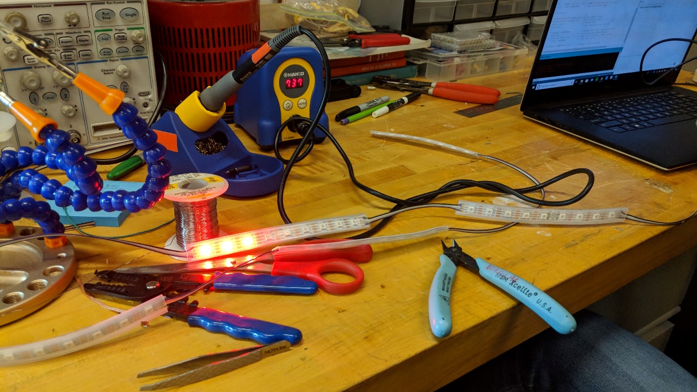
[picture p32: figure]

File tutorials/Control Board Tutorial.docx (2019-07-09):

# Control board Tutorial

# control board parts and schematics

### Parts list for the board:

Part | Amount | Notes
Custom control board | 1 | Can be found in the GitHub at: "GitHub\seeboat\hardware\controlBoard\controlBoard-0.5.brd"
2.7 kΩ resistor, 0603 | 2 | Part number: RNCP0603FTD2K74CT-ND, https://www.digikey.com/products/en?keywords=RNCP0603FTD2K74CT-ND
DPDT switch | 1 | Part number: 401-2013-1-ND, https://www.digikey.com/product-detail/en/AYZ0202AGRLC/401-2013-1-ND/1640122
4-pin header female | 4 | Part number: WM4802-ND, https://www.digikey.com/products/en?keywords=WM4802-ND
3-pin header female | 1 | Part number: WM4801-ND, https://www.digikey.com/products/en?keywords=WM4801-ND
Male headers | 1 | Break to correct size: https://www.adafruit.com/product/392

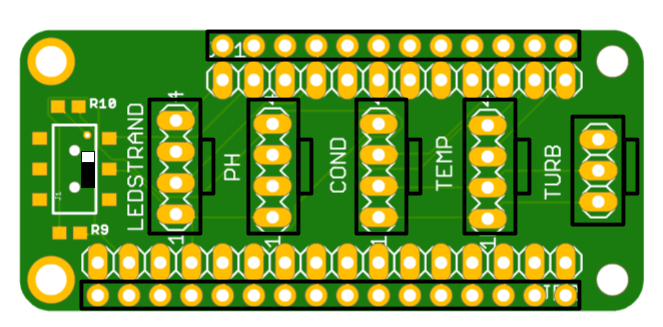
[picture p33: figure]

The schematic above details where each of the parts should go.

# Steps:

1. Solder on resistors, then the switch. Make sure the switch is oriented according to the schematic.
2. Solder on the 4-pin headers and the 3-pin, oriented in the right direction. It’s helpful to just solder one pin, then make sure the header is perpendicular to the board, and then solder the rest.
3. Solder on the male pin legs in the outer holes of the board. It’s helpful to use the female pin counterparts already soldered on a different board to help align the pins correctly. Insert the male pins into the other board, then set the control board on top and solder the pins.
4. All done!

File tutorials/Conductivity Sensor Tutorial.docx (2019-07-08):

# Conductivity Sensor Tutorial/troubleshooting

# Probe

The probe for the conductivity sensor is 3-D printed out of ______. It is the only part of the sensor which should be immersed in water.

## Manufacturing

### Parts list for the probe:

Part | Amount | Notes | Image

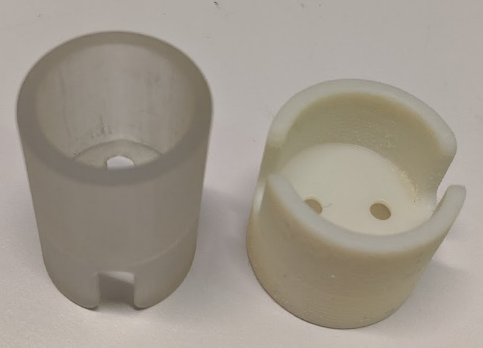
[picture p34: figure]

3D printed probe | 1 | stl file for 3D printing can be found in the Dropbox at: "SeeBoat\Talia\Conductivity\Hardware\probe 2.0.STL"
Single-core wire | 2 | Any single core wire should work, a relatively thin one will be easier to attach.

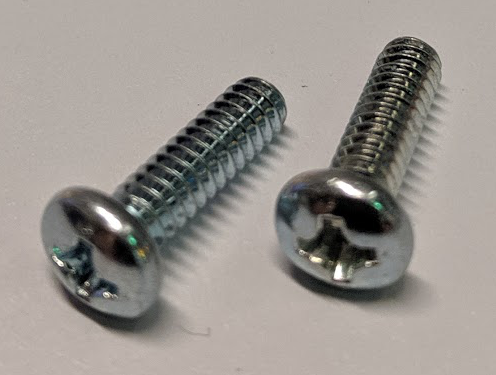
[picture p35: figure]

6-32 ½” screws | 2 | These screws fit the holes in the probe CAD snugly, so they will be the easiest to install.

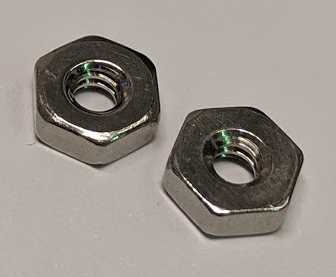
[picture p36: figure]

6-32 ½” nuts | 2 | These are the corresponding nuts.

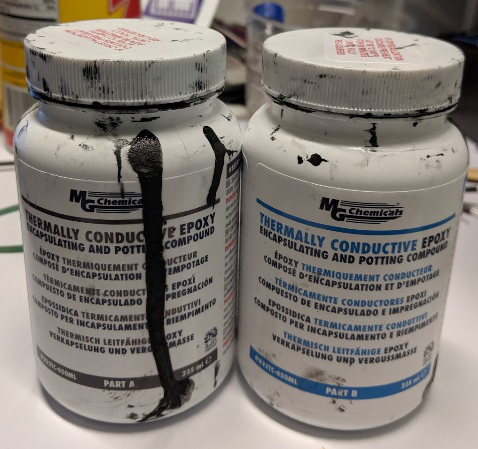
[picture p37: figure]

MG Chemicals epoxy | 1 | Part number: 832TC-450ML https://www.amazon.com/MG-Chemicals-Thermally-Conductive-Encapsulating/dp/B008UH4CRM#product-description-iframe

### Steps:

1) 3D-print the probe using the stl file in the Dropbox folder mentioned above.
2) Gather other materials according to the parts list.
3) Tighten the screws in place, using the nuts. Do not tighten all the way yet.

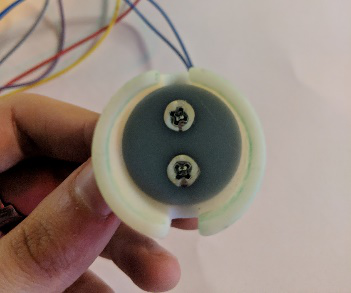
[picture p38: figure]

The head of the screws should be facing as shown above.

4) Carefully wrap exposed wire around each end of the screw, then tighten the nuts on all the way so that the wire is securely clamped down by the nuts.
5) Follow the directions on the epoxy containers to waterproof the probe. The epoxy should cover the threads of the screws and up the wires a little bit.

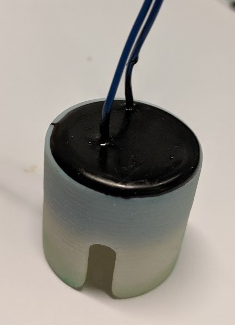
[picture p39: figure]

The cured epoxy (black) should look like this.

6) Connect the ends of the wires to the appropriate pin on the circuit board.

# Circuit Board

The circuit board has a lot of small parts and assembling requires a good amount of patience. Take your time!

## Manufacturing

### Parts list for the circuit board:

Symbol | Value | Part # (if applicable)
R1, R2, R3, R4 | 10 kΩ | YAG2122CT-ND, 0603
R5 | 1 MΩ | YAG4498CT-ND, 0603
R6, R7 | 1 kΩ | RNCP0603FTD1K00CT-ND, 0603
R8 | 47 kΩ | 0603
R9 | 4.7 kΩ | 0603
R10 | 1.2 kΩ | 0603
C2 | 0.1 µF | C1608X8R1H104K080AB, 0603
D1, D2 | N/A | S1BBFDICTND
U1 | N/A | TLV2374IDR
U2 | N/A | TLE2426CLPR
IC1 | N/A | AD8655ARZ-REEL7CT-ND
S1 | N/A | 401-2013-1-ND
-- | N/A | custom circuit board
Header | N/A | WM9131-ND

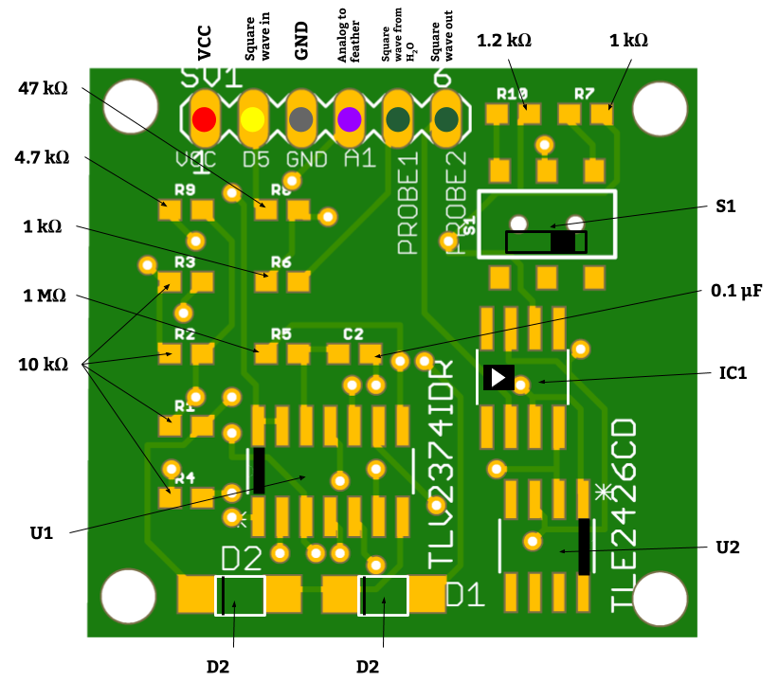
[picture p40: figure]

### Steps:

1) Collect all the parts you need to solder on a print-out of the above schematic (located in the Dropbox at: “SeeBoat\Talia\Conductivity\Hardware\Conductivity Board Diagram.docx”). It helps to tape them to their corresponding labels so you don’t mix them up.
2) Solder each part onto the board.

NOTE: Some of the parts have directionality to them, so make sure you have them oriented the right way. Also, it helps to start adding parts from the middle and then work your way to the edges.

3) Solder the wires which connect to the Feather into header. The order in which you solder them is very important, so be sure to double check they match:

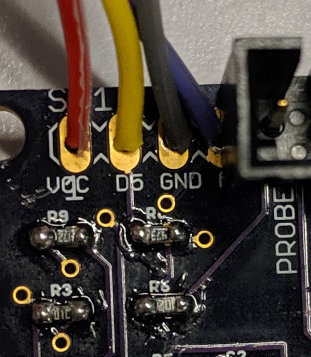
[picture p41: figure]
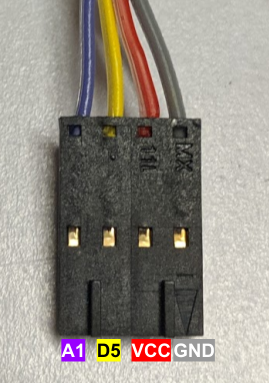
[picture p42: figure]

This is the correct ordering of the wires.

4) Solder the wires which connect to the probe into their pins.
5) Test it!

## Calibration

To calibrate the conductivity sensor, use the conductivity standards to map the voltage readings to the corresponding conductivities. You can see the past calibrations in the Voltage to Conductivity spreadsheet (located in the Dropbox at: " SeeBoat\Talia\Conductivity\Voltage to Conductivity.xlsx").

To measure the voltage, use the Arduino code in conductivity.ino (located in the Github at: "seeboat\software\testing\conductivity\conductivity.ino"). Change the code to output voltage instead of conductivity in the loop():

>> Serial.println(conductivity);

Change to:

>> Serial.println(voltage);

An example calibration:

Voltage (V)
Conductivity (µS/cm) | Switch towards middle (1.2 kΩ) | Average Voltage | Switch towards edge (1 kΩ) | Average Voltage
50.14214171 | 0.01-0.02 | 0.015 | 0.01-0.02 | 0.015
100 | 0.01-0.03 | 0.02 | 0.01-0.02 | 0.015
700 | 0.08-0.10 | 0.09 | 0.06-0.08 | 0.07
843.4624552 | 0.15-0.16 | 0.155 | 0.14-0.15 | 0.145
2000 | 0.21-0.24 | 0.225 | 0.18-0.20 | 0.19
3000 | 0.38-0.41 | 0.395 | 0.27-0.28 | 0.275
7688.461729 | 0.92-0.93 | 0.925 | 0.77-0.78 | 0.775

Linear regression shows the relationship between the data:

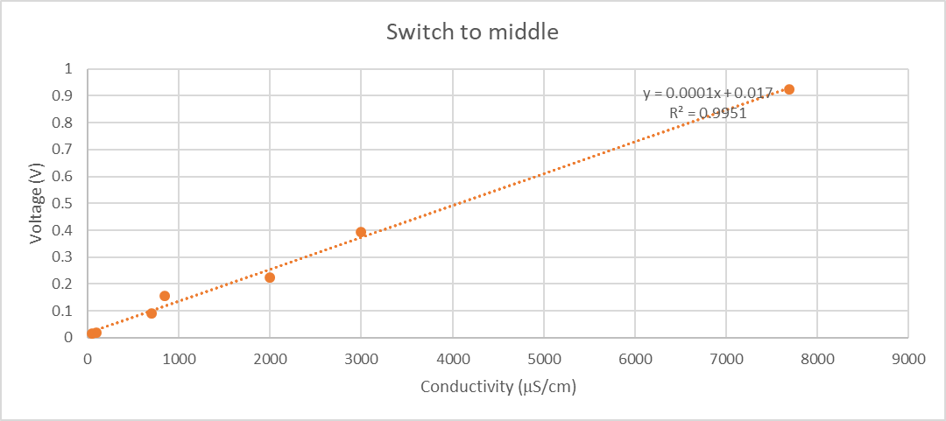
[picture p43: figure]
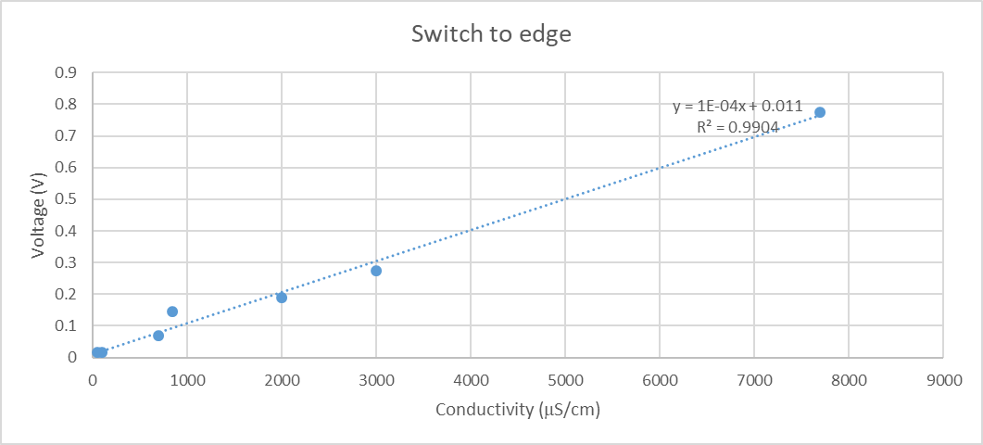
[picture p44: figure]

NOTE: Some of the standards are in µS, some in µS/cm. To make sure all the units are consistent, multiply/divide by the cell constant. Our cell constant is approximately 0.5-1 cm⁻¹.

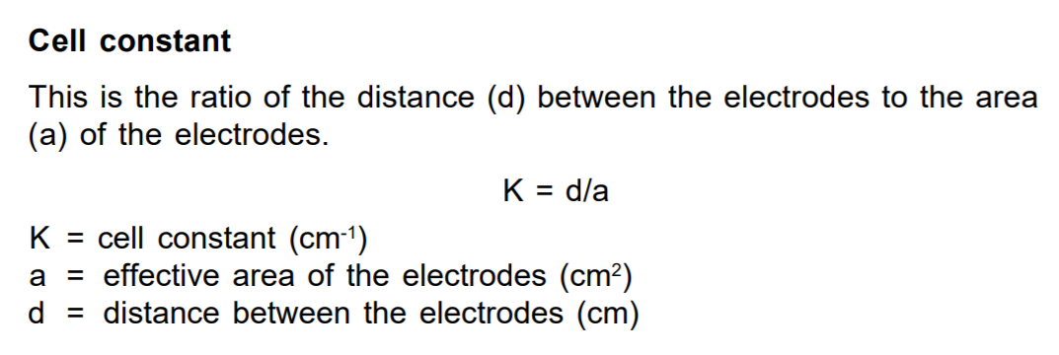
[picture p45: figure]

From: http://www.analytical-chemistry.uoc.gr/files/items/6/618/agwgimometria_2.pdf

# Troubleshooting

Troubleshooting the conductivity circuit board often involves using an oscilloscope. Follow the diagram below to debug what the problem might be:

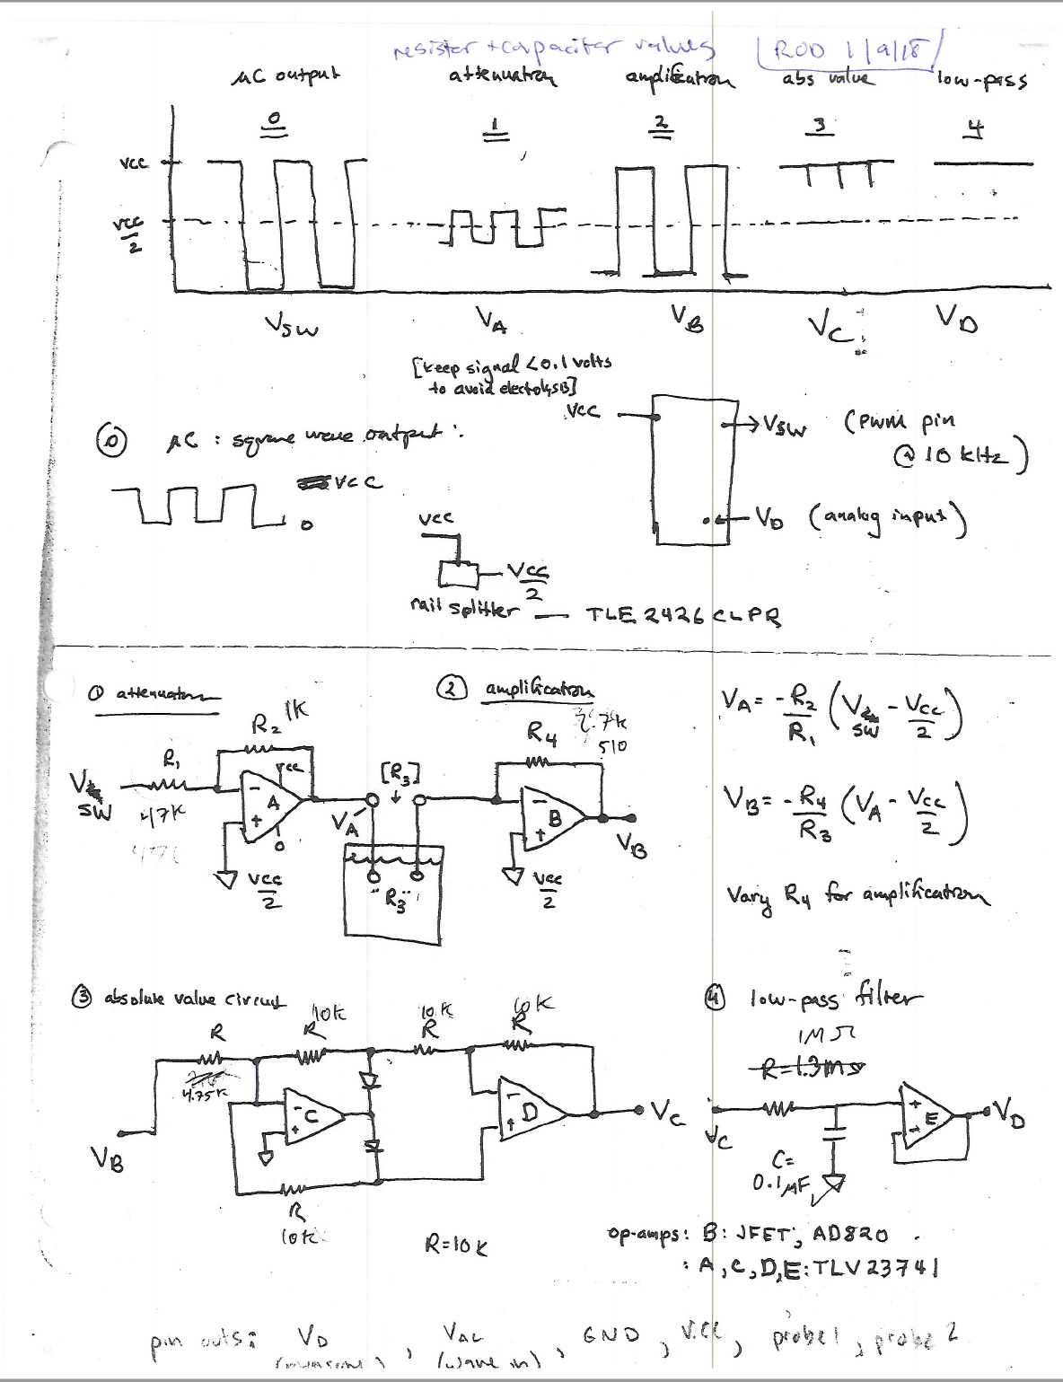
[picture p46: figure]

From: “SeeBoat\Talia\Conductivity\conductivityCircuitValues.pdf"

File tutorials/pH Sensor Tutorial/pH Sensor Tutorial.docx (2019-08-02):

# pH Sensor tutorial

# assembling/wiring

**NOTE: Our pH sensor is wired using I²C mode, NOT UART mode. Follow the directions accordingly.** Wire the board following the directions in the documents located in the Github at: "GitHub\seeboat\tutorials\pH Sensor Tutorial\ezo-ph-wiringdiagram.pdf" and "GitHub\seeboat\tutorials\pH Sensor Tutorial\pH_EZO_Datasheet.pdf." Use the photos below to be sure you are wiring the pins correctly to the header. It helps to use the same colored wire, too. The wire can be rather short (ours is about 4 inches long) because the pH probe comes with a long lead.

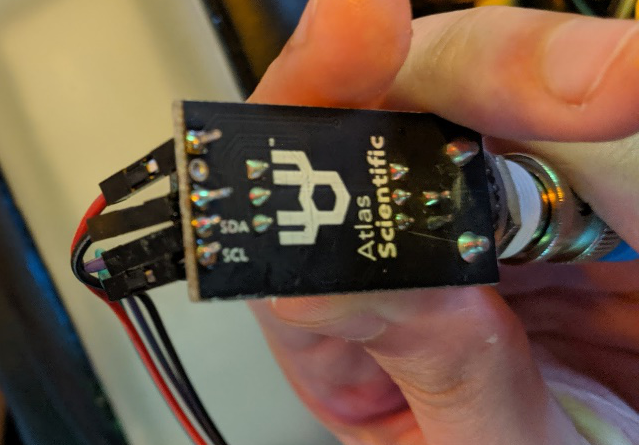
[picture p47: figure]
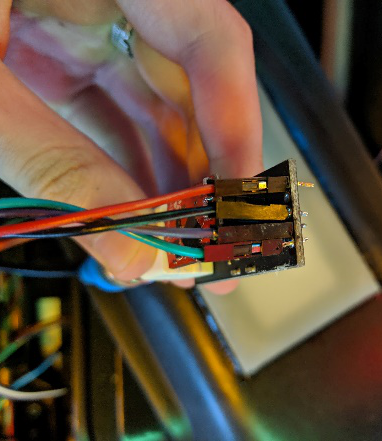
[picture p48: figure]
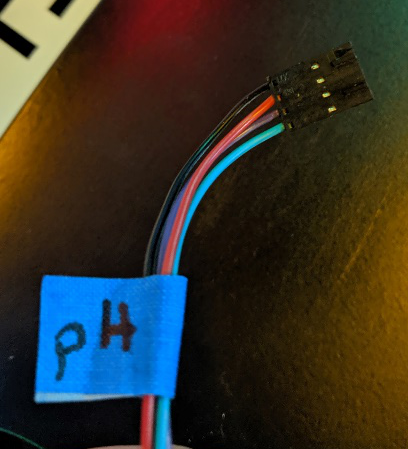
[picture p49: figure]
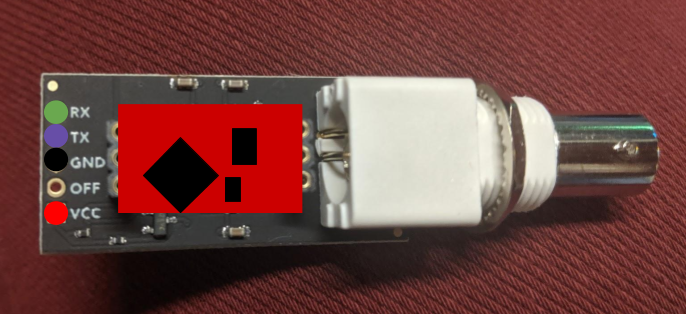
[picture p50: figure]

# Switching from uart to i²C

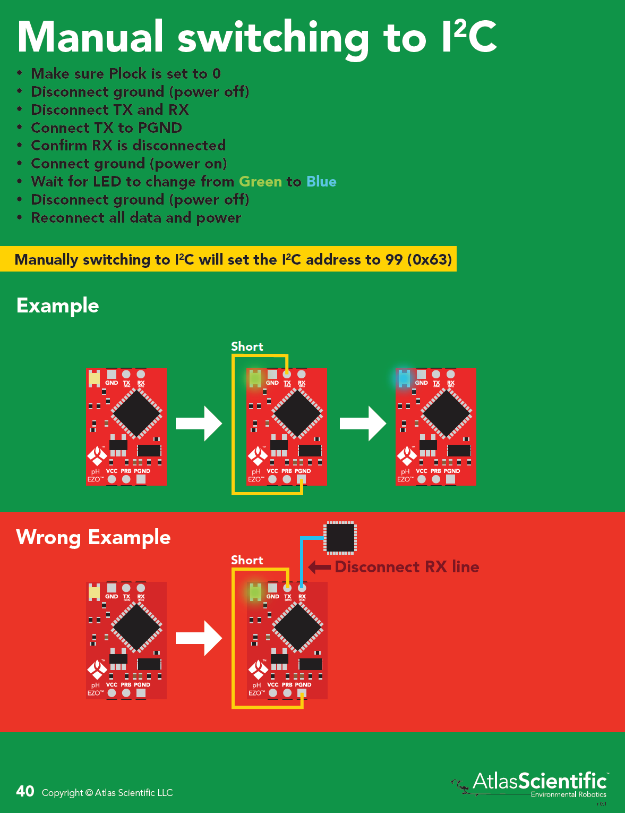
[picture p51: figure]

# calibrating

Follow the directions in the recalibration document if the pH sensor doesn’t seem to measuring reasonable values. The document can be found in the GitHub at: "GitHub\seeboat\tutorials\pH Sensor Tutorial\pH_reconditioning_kit_instructions.pdf."

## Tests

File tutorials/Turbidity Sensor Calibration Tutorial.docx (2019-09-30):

# Turbidity Calibration Tutorial

# set up

In order to calibrate your turbidity sensor, you’ll need:

- Electronics
  - Feather M0 LoRa Radio
  - Breakout board for Feather
  - MicroUSB cable
  - Uncalibrated, waterproofed turbidity sensors
- Permanent marker and tape for labeling
- Supplies for making dark boxes
  - Black foam board
  - Tape or hot glue
  - Pen that writes on black
  - 3D printer or small container and black spray paint
- Supplies for making standards
  - Lots of identical, tiny, glass jars
  - Formazin
  - Distilled water
  - 10 mL, 1mL pipettes
  - 100 mL volumetric flask
  - Enough graduated cylinders for all the standards
  - Cutting oil
  - Larger containers
  - Tissues

# Making formazin standards

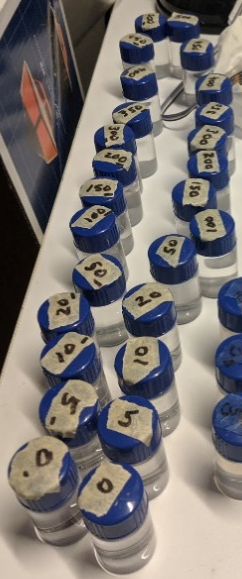
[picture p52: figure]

1. Download information booklet: https://sea.hach.com/formazin-turbidity-standard-4000-ntu-500-ml/product-downloads?id=26514554120.
2. Navigate to “Appendix II. Preparing Formazin Dilutions,” on page 13.
3. We made dilutions ranging from 0-500 NTU, incrementing by 50 NTU.
  i. Make sure all the tiny vials are the same.
  ii. Make a total of two vials for each data point in order to average data later on.
    i. Swirl the standard solution before splitting between the two vials.
    ii. Distinguish between the solutions somehow; we added a dash to one vial in each pair.
  iii. Make sure to label each vial with the correct number of NTUs.
4. Wipe down all the vials with tissues so that there is nothing that might disrupt the sensor readings.

# Making dark box

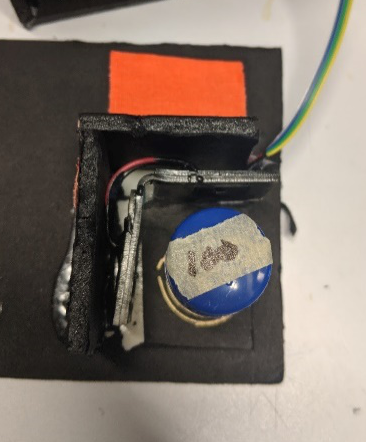
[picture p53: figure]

1. Cut out from the foam board: a platform, a 90°-angled notch for sensor, walls for the box, and a cover/top.
  a. Make sure to leave room for wires.
2. Use tape or hot glue to connect the walls and top together, and the notch and platform together.
3. Put one sensor in, and figure out where intersection of sensor/LED paths are. Place a vial there and draw a circle around the vial.

# measuring and recording data

1. Design the spreadsheet for collecting the data.
  i. The labels are: sensor, standard.NTU, test.type, sample.label, media, ave.freq.kHz, irradiance.mW.cm².

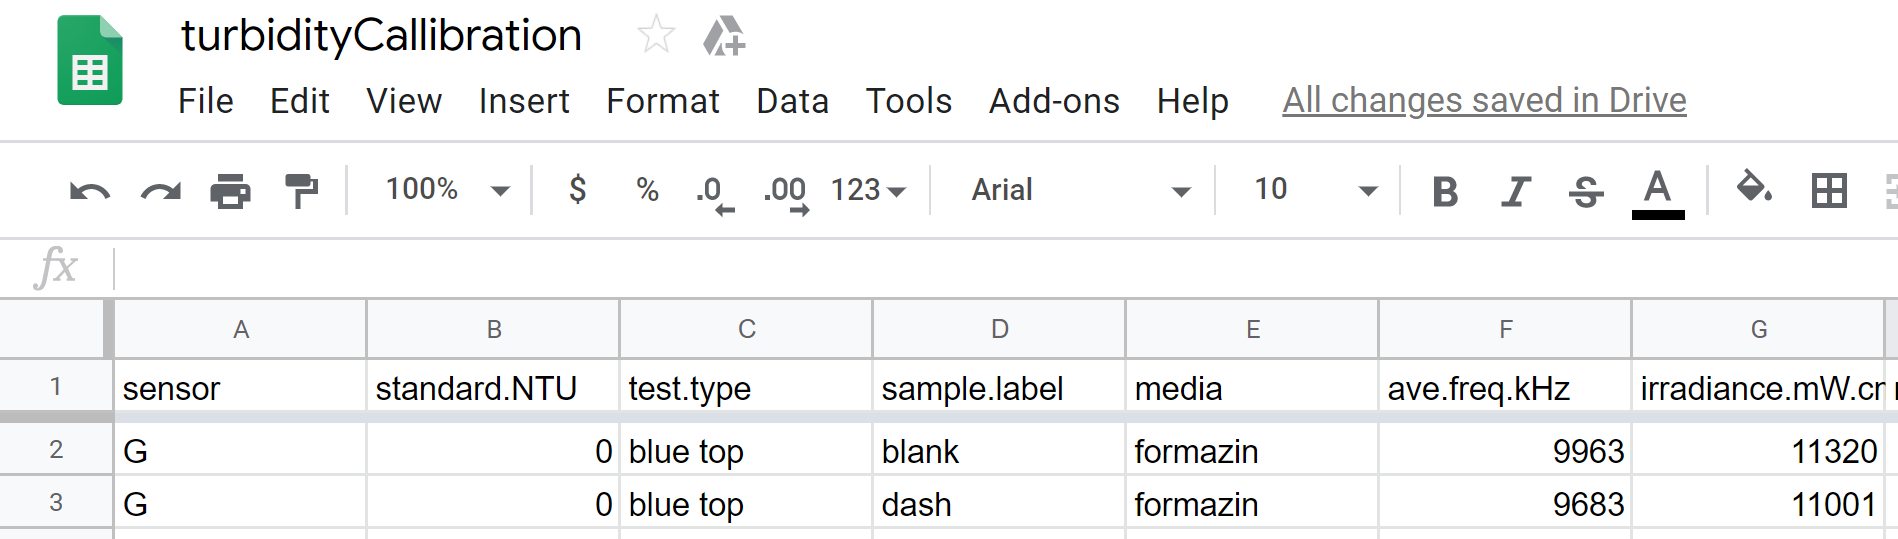
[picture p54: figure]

2. Use the turbidity code on GitHub: "GitHub\seeboat\software\testing\turbidity\turbidity.ino."
3. Turn off all the lights in the room, and make sure there are no weird shadows over the box.

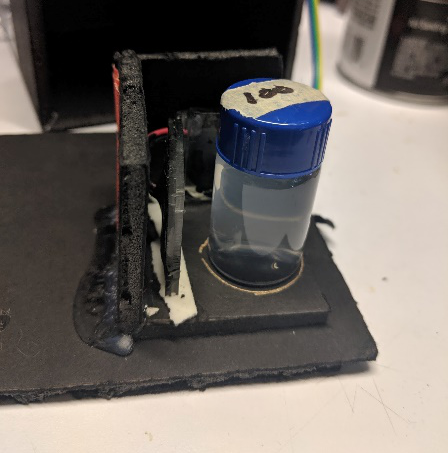
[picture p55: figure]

4. Measure ave.freq.kHz and irradiance.mW.cm² for each vial, moving from low to high. Mark the values in the spreadsheet. Don’t move the sensor during calibration; change the vial not the sensor.
  i. Make sure the vial is centered.
  ii. Make sure mixture is distributed (invert and swirl if not).
  iii. Make sure there are no fingerprints on the vial.
  iv. Stick down the sensor securely.
  v. Check that the center of the vial is still correct between sensors.
  vi. Make sure the box is sufficiently blocking light.
  vii. Let the data stabilize before recording values.

# cutting oil secondary standards

1. Based on the first sensor’s data, try to hit roughly the same range of cloudiness as the data.

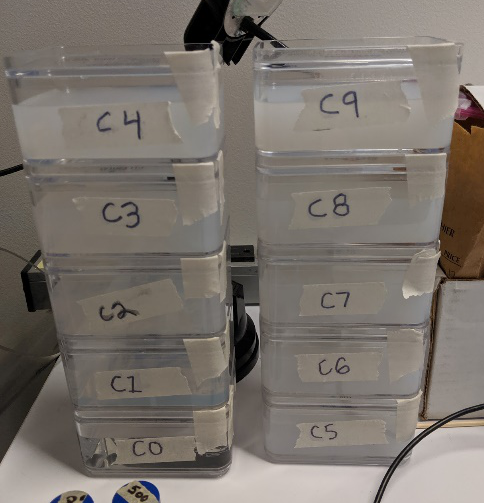
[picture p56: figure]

i. Continue to dilute the mixture, and continue to measure the value with the sensor to see how close you are to the minimum, or maximum of the data endpoints.

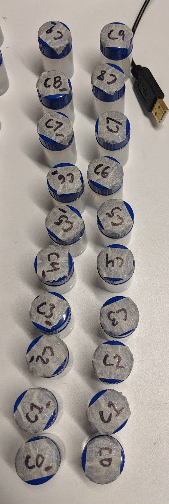
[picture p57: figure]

2. Make a full larger container of each data point large enough to fully submerge sensor in, and two small vials per data point.
3. Label CUT1, CUT2…
4. Measure the small vials of cutting oil with the first sensor still in place, and record in the spreadsheet.
5. Reference: https://www.mdpi.com/1424-8220/14/4/7142.

## record data for each sensor!

# Data analysis

1. Make an xy scatter plot for each sensor.
2. Fit a regression curve for all the formazin data points.
3. Add the cutting oil data points, back-calculate the NTU for cutting oil standards.
  a. Should now have NTU values for CUT1, CUT2…
4. See how consistent sensors are with cutting oil NTUs.
5. Compute percent differences between the two vials in each pair, see if there are consistencies across sensors.
6. Check if any data looks weird overall.
7. Identify sensors’ precision within certain ranges.
8. Discard sensors based on bad fit, weird regression lines, etc.

# Calibrate for free water use

1. 3D-print a box large enough to fit each sensor in with matte, black material.
2. Pour one cutting oil large container into the black 3D printed box.

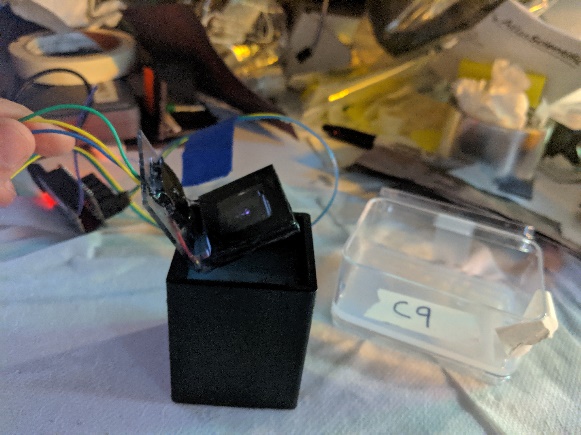
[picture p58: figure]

3. Submerge each sensor in the box (change the sensor not the solution).
4. Cover the box with black paper to block light.
5. Record ave.freq.kHz and irradiance.mW.cm² in the spreadsheet.
6. Repeat steps 1-3 for each sensor to get two data points.
7. Wipe down the sensor to remove oil.

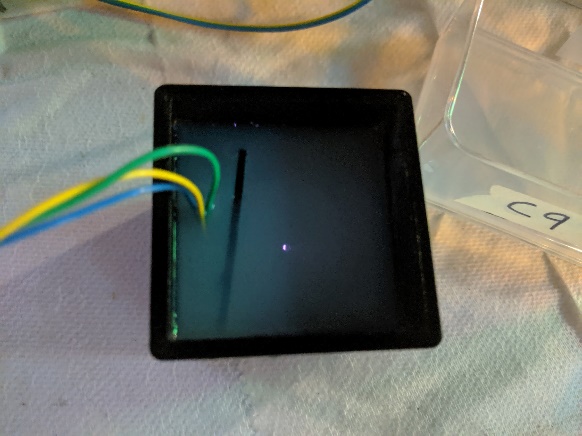
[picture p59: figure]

8. Calculate for each sensor the equation to get free water NTU based on Arduino readings.

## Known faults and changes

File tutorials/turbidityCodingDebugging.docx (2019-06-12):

======= NOTES ON THE TURBIDITY CODE & DEBUGGING THE SENSOR =========

LAURA TO DO: ADD THE CUT FILES FOR THE ACRYLIC

The code is in the Dropbox. It should work on both an Arduino Uno and a Adafruit feather M0 LoRa radio board.

If you cover the sensor up, the code will slow down a lot and lag.

If the code doesn’t run at all, the sensor might not be connected right.

The code will still run even if the LED isn’t working. Make sure to visually check that the LED is on--you should be able to see it no matter what the lighting is like. You can see a red dot with your eyes (or phone).

Make sure you connect to digital pin 10.

======================== NOTES ON TESTING THE SENSOR ================

LAURA TO DO: TURBIDITY STANDARDS AND CALIBRATION

LAURA TO DO: TEST WHILE SUBMERGED IN WATER

LAURA TO DO: TEST IF THE VALUES CHANGE IF THE WATER MOVES AROUND

LAURA TO DO: WHICH BOAT TO ATTACH TO AND HOW? CHECK ROBUSTNESS OF BOAT

The sensor needs to be in the dark in order to get reasonable values for testing. Use the black foam core box for this.

If there isn’t anything (e.g. water sample) between the sensor and the LED, you will get really high readings.

Make sure the sample location (between the sensor and the LED) is standardized so you get consistent values.

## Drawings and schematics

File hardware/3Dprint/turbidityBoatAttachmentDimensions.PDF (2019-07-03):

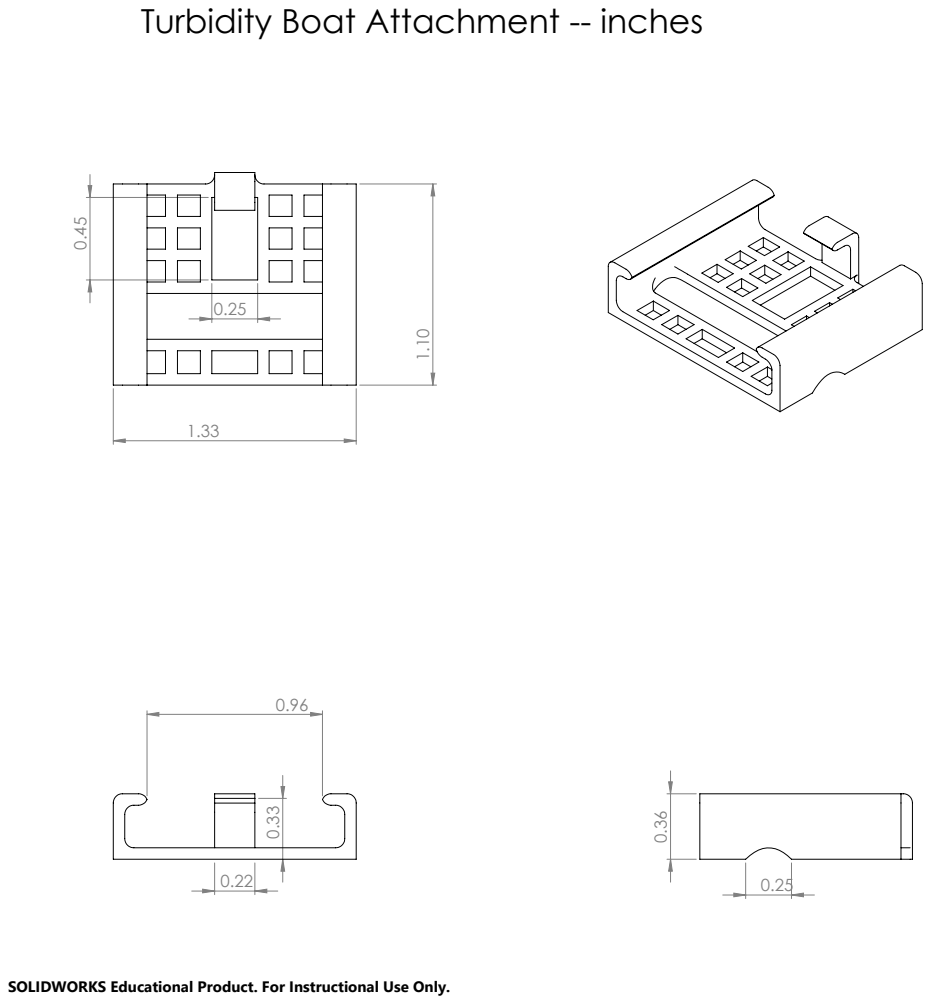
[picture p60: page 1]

Turbidity Boat Attachment -- inches

SOLIDWORKS Educational Product. For Instructional Use Only.

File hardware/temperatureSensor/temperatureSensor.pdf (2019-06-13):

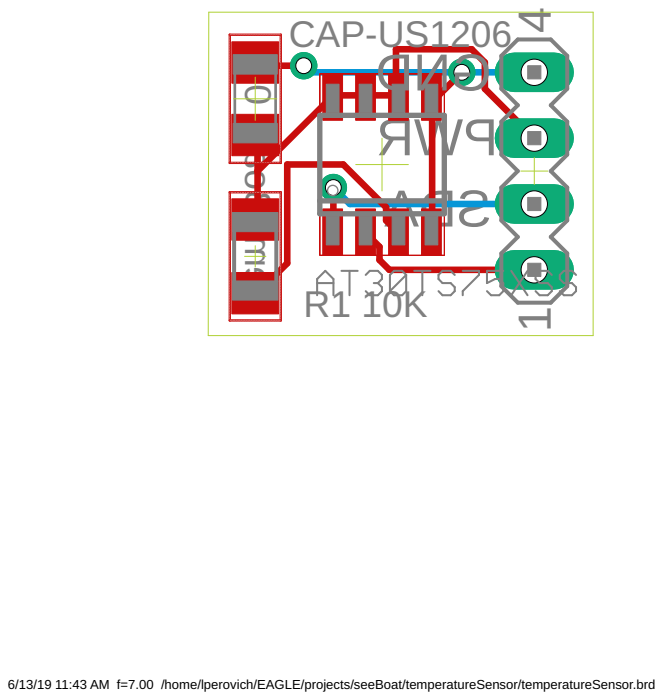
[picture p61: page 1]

6/13/19 11:43 AM f=7.00 /home/lperovich/EAGLE/projects/seeBoat/temperatureSensor/temperatureSensor.brd

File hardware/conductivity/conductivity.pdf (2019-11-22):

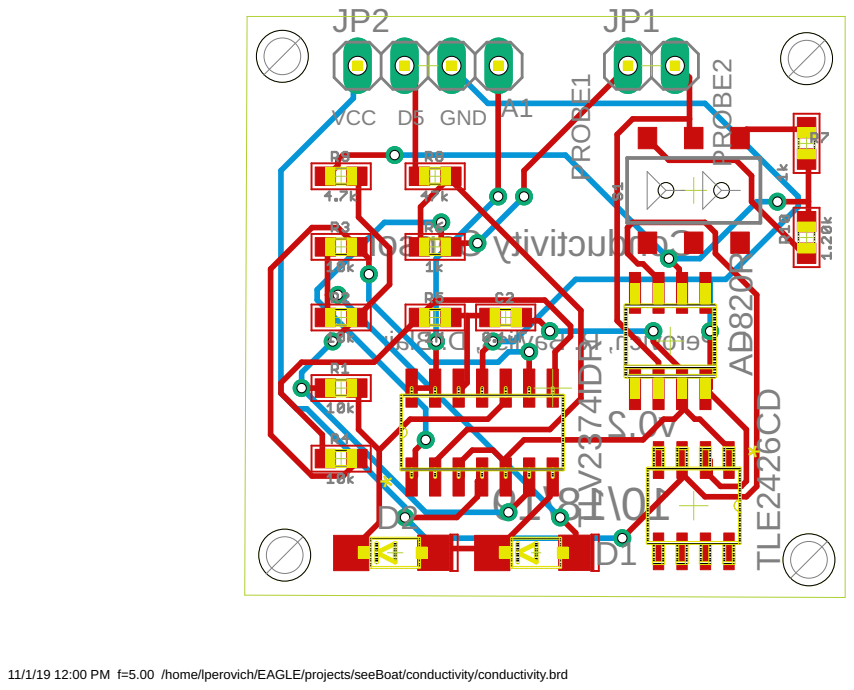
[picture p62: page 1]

11/1/19 12:00 PM f=5.00 /home/lperovich/EAGLE/projects/seeBoat/conductivity/conductivity.brd

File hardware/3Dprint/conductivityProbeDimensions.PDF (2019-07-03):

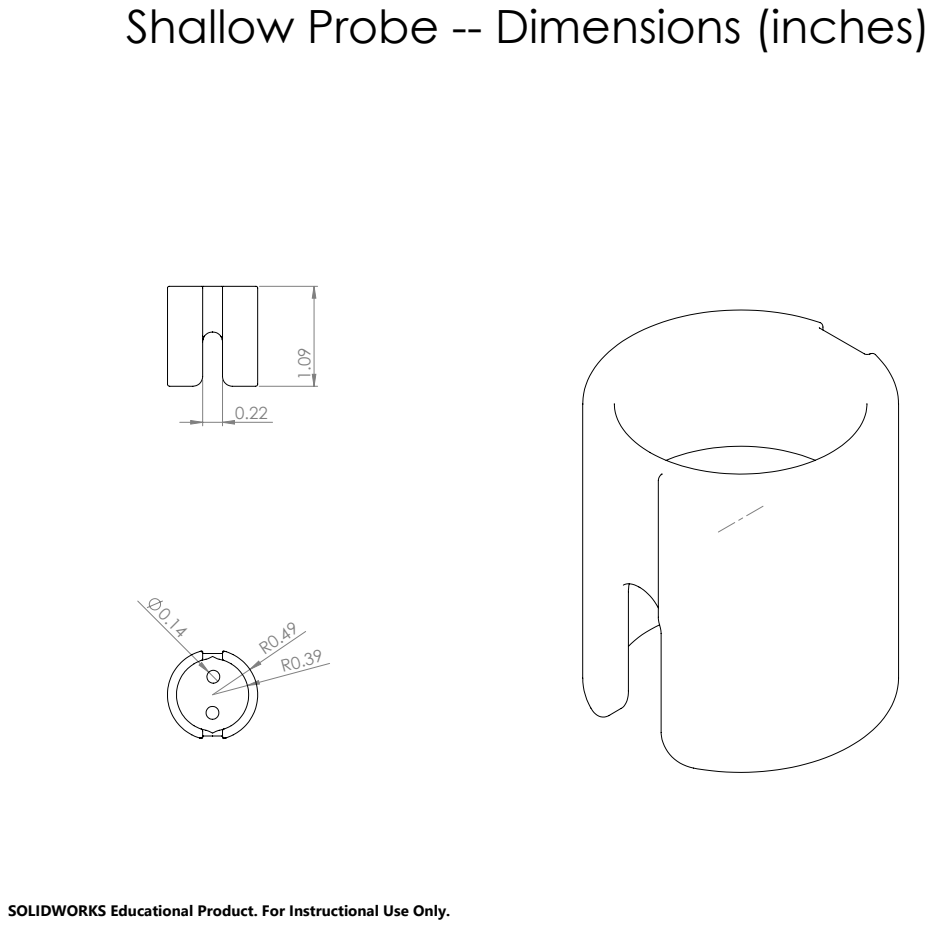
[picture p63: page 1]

Shallow Probe -- Dimensions (inches)

SOLIDWORKS Educational Product. For Instructional Use Only.

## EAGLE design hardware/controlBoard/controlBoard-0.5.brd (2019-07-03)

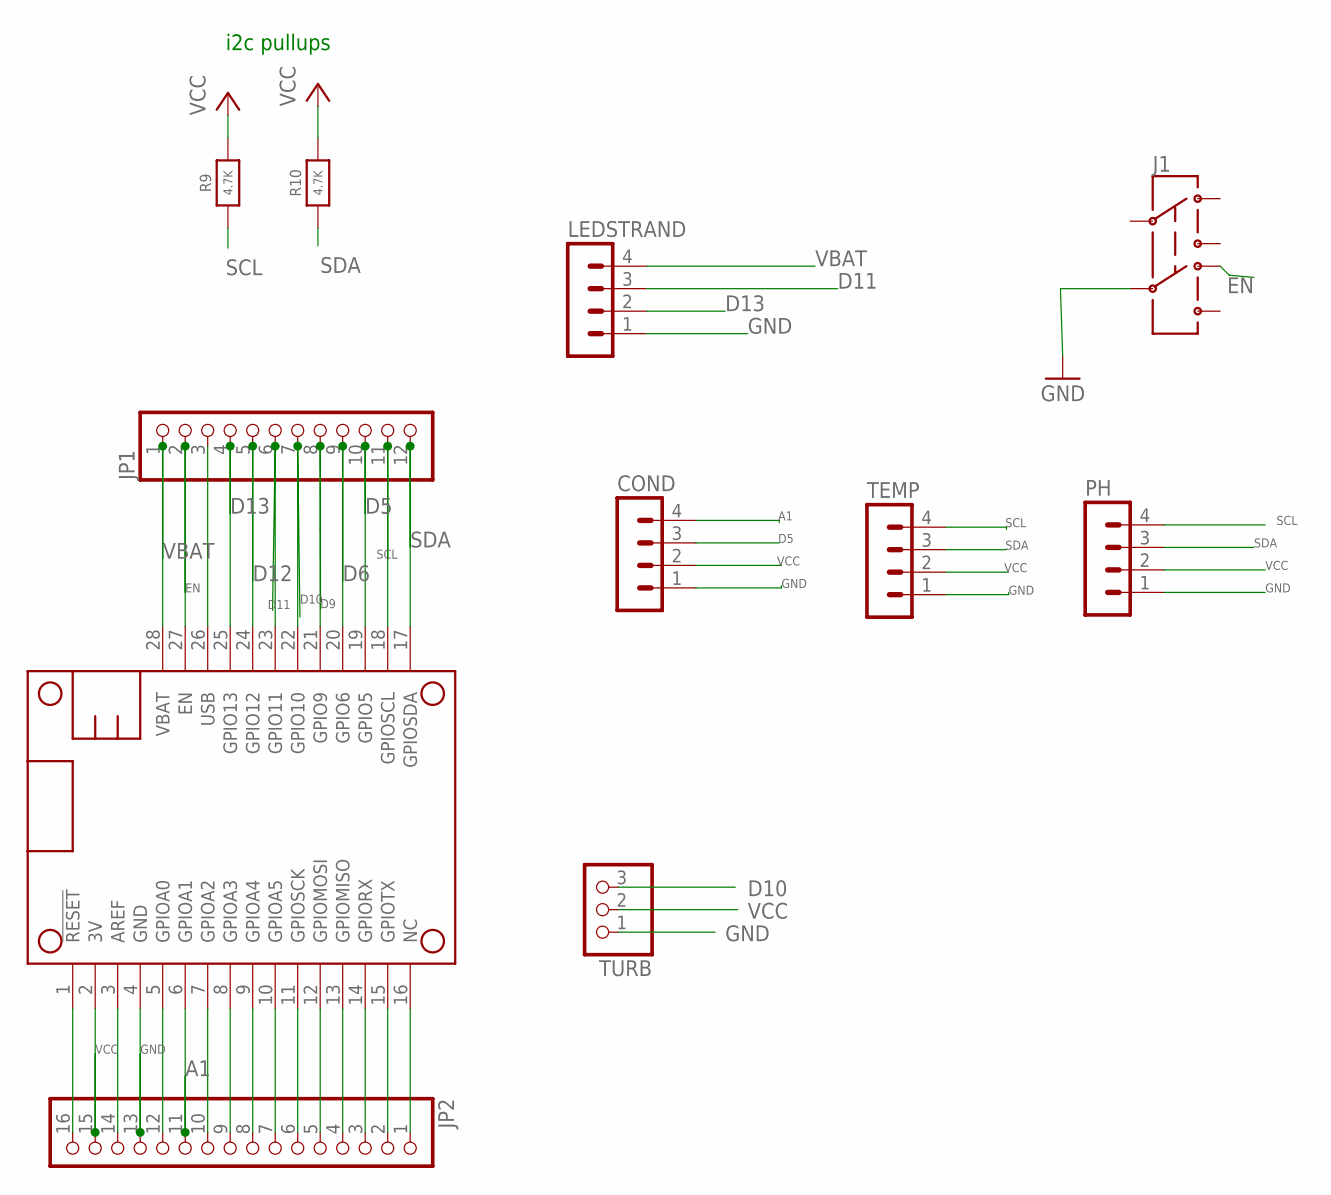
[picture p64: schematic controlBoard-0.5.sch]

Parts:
COND: MA04-1
J1: AYZ0202
JP1: PINHD-1X12; 1X12
JP2: PINHD-1X16; 1X16
LEDSTRAND: MA04-1
MS1: FEATHERWING
PH: MA04-1
R9, R10: 4.7K; 0603-NO
TEMP: MA04-1
TURB: PINHD-1X3; 1X03

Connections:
A1: COND.4, JP2.11, MS1.6 (GPIOA1)
D5: COND.3, JP1.10, MS1.19 (GPIO5)
D6: JP1.9, MS1.20 (GPIO6)
D9: JP1.8, MS1.21 (GPIO9)
D10: JP1.7, MS1.22 (GPIO10), TURB.3
D11: JP1.6, LEDSTRAND.3, MS1.23 (GPIO11)
D12: JP1.5, MS1.24 (GPIO12)
D13: JP1.4, LEDSTRAND.2, MS1.25 (GPIO13)
EN: J1.6 (4), JP1.2, MS1.27 (EN)
GND: COND.1, J1.5, JP2.13, LEDSTRAND.1, MS1.4 (GND), PH.1, TEMP.1, TURB.1
unnamed: JP2.1, MS1.16 (NC)
unnamed: JP2.2, MS1.15 (GPIOTX)
unnamed: JP2.3, MS1.14 (GPIORX)
unnamed: JP2.4, MS1.13 (GPIOMISO)
unnamed: JP2.5, MS1.12 (GPIOMOSI)
unnamed: JP2.6, MS1.11 (GPIOSCK)
unnamed: JP2.7, MS1.10 (GPIOA5)
unnamed: JP2.8, MS1.9 (GPIOA4)
unnamed: JP2.9, MS1.8 (GPIOA3)
unnamed: JP2.10, MS1.7 (GPIOA2)
unnamed: JP2.12, MS1.5 (GPIOA0)
unnamed: JP2.14, MS1.3 (AREF)
unnamed: JP2.16, MS1.1 (!RESET)
SCL: JP1.11, MS1.18 (GPIOSCL), PH.4, R9.1, TEMP.4
SDA: JP1.12, MS1.17 (GPIOSDA), PH.3, R10.1, TEMP.3
USB: JP1.3, MS1.26 (USB)
VBAT: JP1.1, LEDSTRAND.4, MS1.28 (VBAT)
VCC: COND.2, JP2.15, MS1.2 (3V), PH.2, R9.2, R10.2, TEMP.2, TURB.2

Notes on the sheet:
i2c pullups

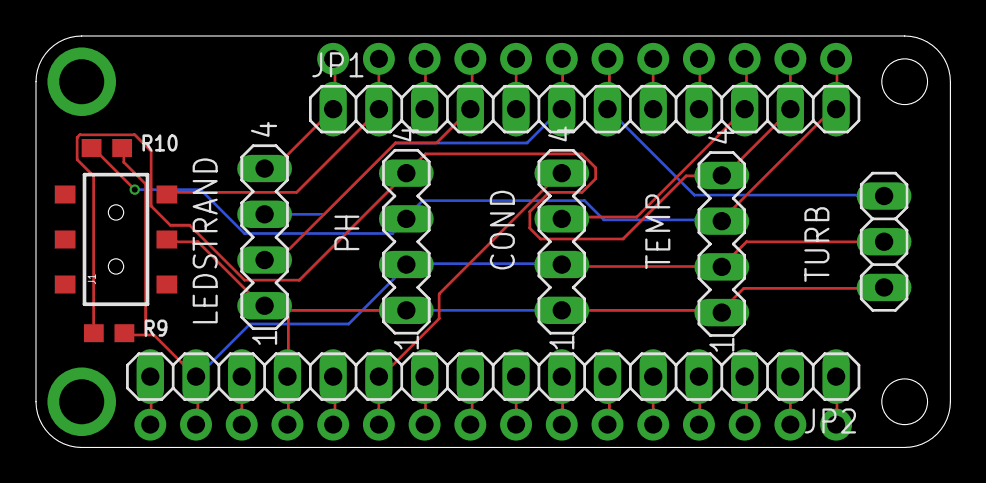
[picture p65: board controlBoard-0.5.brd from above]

Board: 2 copper layers, 50.8 x 22.9 mm, 11 parts (0 on the bottom side), 28 nets.

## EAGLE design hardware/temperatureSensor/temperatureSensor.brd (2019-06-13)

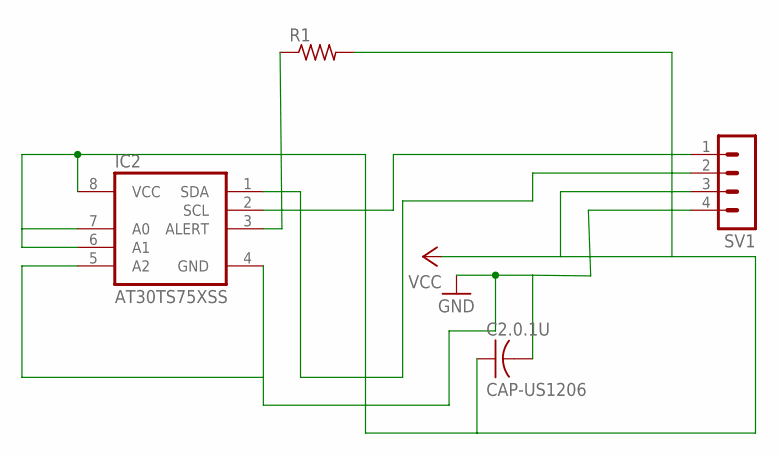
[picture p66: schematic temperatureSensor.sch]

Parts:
C2.0.1U: CAP-US1206; C1206
IC2: AT30TS75XSS; SO8
R1: RES-US1206; R1206
SV1: MA04-1

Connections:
D2: IC2.3 (ALERT), R1.1
GND: C2.0.1U.2, IC2.4 (GND), IC2.5 (A2), SV1.4
unnamed: IC2.2 (SCL), SV1.1
SDA: IC2.1 (SDA), SV1.2
VCC: C2.0.1U.1, IC2.6 (A1), IC2.7 (A0), IC2.8 (VCC), R1.2, SV1.3

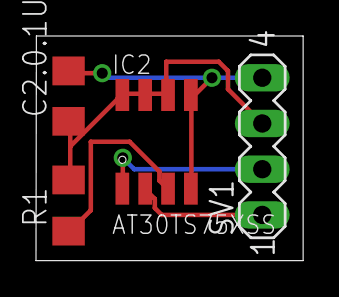
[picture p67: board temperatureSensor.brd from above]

Board: 2 copper layers, 14.8 x 12.5 mm, 4 parts (0 on the bottom side), 5 nets.

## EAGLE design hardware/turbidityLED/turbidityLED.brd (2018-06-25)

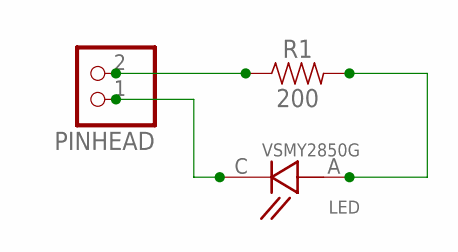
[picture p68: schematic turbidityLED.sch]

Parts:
LED: VSMY2850G; SOD4223X279N
PINHEAD: PINHD-1X2; 1X02
R1: 200; 0603

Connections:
unnamed: PINHEAD.2, R1.1
unnamed: LED.A, R1.2
unnamed: LED.C, PINHEAD.1

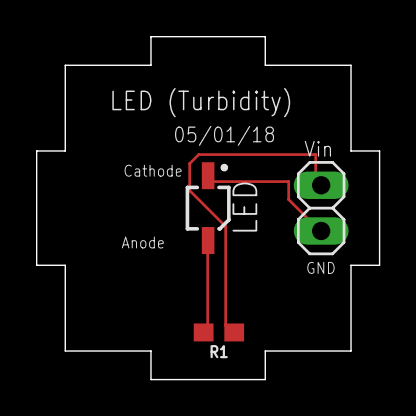
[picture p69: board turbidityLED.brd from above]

Board: 2 copper layers, 19.1 x 19.1 mm, 3 parts (0 on the bottom side), 3 nets.

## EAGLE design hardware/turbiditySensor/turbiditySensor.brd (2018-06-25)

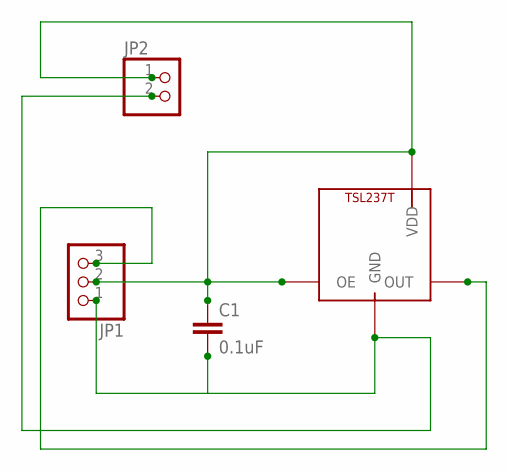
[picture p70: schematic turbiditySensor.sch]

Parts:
C1: 0.1uF; 0603
JP1: PINHD-1X3; 1X03
JP2: PINHD-1X2; 1X02
SENSOR: WS2812B3535; LED3535

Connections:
unnamed: JP1.3, SENSOR.4 (OUT)
unnamed: C1.1, JP1.2, JP2.1, SENSOR.1 (OE), SENSOR.3 (VDD)
unnamed: C1.2, JP1.1, JP2.2, SENSOR.2 (GND)

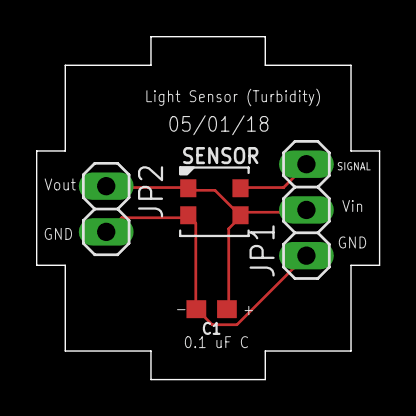
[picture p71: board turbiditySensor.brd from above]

Board: 2 copper layers, 19.1 x 19.1 mm, 4 parts (0 on the bottom side), 3 nets.

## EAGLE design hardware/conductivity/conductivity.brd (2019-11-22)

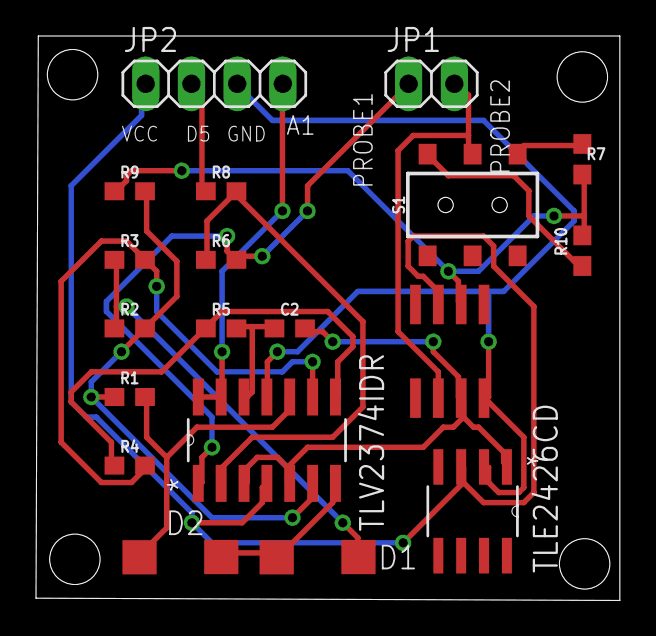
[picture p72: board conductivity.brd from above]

Board: 2 copper layers, 32.4 x 31.4 mm, 19 parts (0 on the bottom side), 18 nets.

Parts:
C2: 0.1uF; 0603
D1, D2: SOD123
IC1: AD820R; SO8
JP1: 1X02
JP2: 1X04
R1, R2, R3, R4: 10k; 0603
R5: 1M; 0603
R6, R7: 1k; 0603
R8: 47k; 0603
R9: 4.7k; 0603
R10: 1.20k; 0603
S1: SWITCH_DPDT_SMD_AYZ0202
U1: TLV2374IDR; SOIC127P600X175-14N
U2: TLE2426CD; SOIC127P600X175-8N

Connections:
FROMWATER: IC1.2, JP1.2, S1.2
unnamed: IC1.7, JP2.1, U1.4, U2.3
unnamed: R10.1, S1.1
unnamed: C2.2, IC1.3, U1.3, U1.5, U2.1
unnamed: R6.1, R8.2, U1.2
unnamed: IC1.6, R7.2, R9.1, R10.2
unnamed: R1.1, R2.2, R9.2, U1.6
unnamed: D1.ANODE, R2.1, R3.1
unnamed: D1.CATHODE, D2.ANODE, U1.7
unnamed: D2.CATHODE, R1.2, U1.10
unnamed: R3.2, R4.2, U1.9
unnamed: R4.1, R5.1, U1.8
unnamed: C2.1, R5.2, U1.12
unnamed: JP2.4, U1.13, U1.14
unnamed: JP2.2, R8.1
unnamed: IC1.4, JP2.3, U1.11, U2.2
unnamed: JP1.1, R6.2, U1.1
unnamed: R7.1, S1.3

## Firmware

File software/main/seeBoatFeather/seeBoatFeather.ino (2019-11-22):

//Code by Laura
//Started June 2017
//Attempt to get the seeBoat from feather working

//Edits from Rod Fall 2017
//Revised the turbidty part
//Add pH part
//Added the conductivity part
//Data assemble all goes together now
//watch out for the timing in the pH probe--wrong timing means we'll see zero values
//GPS worked okay as long as all the I2C stuff was plugged in okay, didn't see any weird dropping off behavior

//Edits from Talia Spring/Summer 2019
//Updated conductivity code.
//LED strip works with all data types.
//Integrated all components.
//Verified that transmitter/reciever functions work.
//Added multi-boat functionality.

//Parts:
//feather radio: sents data to central feather attached to computer
//feather GPS module: time and location data
//seeBoat breakout:
//+water +temperature +conductivity +turbidity
//+LED color changing
//+turns data into something that can be sent

//////////////////////////////////////////////////////////////////////////////////////////////////
// Resolved: MUST SWTICH FROM I2C library to WIRE library!! (for temp sensor). M0 doesn't like I2C, GPS HATES DELAYS, WE MUST GET RID OF THEM!!
// Resolved: ??what's the best format for this actually? (GPS data format)
//////////////////////////////////////////////////////////////////////////////////////////////////


#include <Wire.h>
#include <RH_RF95.h>
#include <math.h>
#include <Arduino.h>
#include <Adafruit_GPS.h>
//#include "SoftPWM.h"
//For radio
#include <SPI.h>
//For radio sleep
#include <Adafruit_DotStar.h> //LED Strip Library
//#include <RGBConverter.h>
//GPS stuff
//Adafruit_GPS GPS(&Serial1);
#define GPSSerial Serial1
//#define GPS Serial1
#define address 99 //This is the wire address for our pH sensor 
// Connect to the GPS on the hardware port
Adafruit_GPS GPS(&GPSSerial);
//Adafruit_GPS GPS;

// Set GPSECHO to 'false' to turn off echoing the GPS data to the Serial console
// Set to 'true' if you want to debug and listen to the raw GPS sentences
#define GPSECHO false
//#define GPSECHO true

////////////////////////////////////////////////////////////////////////////////////////////////////////////////////////////////////////////////////////////
////////////////////////////////////////////////////////////////////////////////////////////////////////////////////////////////////////////////////////////

// HERE'S WHERE YOU CHANGE ALL YOUR VARIABLES: WHAT SENSOR CONTROLS THE LIGHTS? WHAT'S THE RANGE FOR EACH SENSOR? WHICH SENSORS ARE PLUGGED IN?

////////////////////////////////////////////////////////////////////////////////////////////////////////////////////////////////////////////////////////////
////////////////////////////////////////////////////////////////////////////////////////////////////////////////////////////////////////////////////////////

// type the name of the boat here so the code updates to the correct calibrations of the sensors
// options right now are "turtle", "dolphin", or "shark"
//String boatName = "turtle"; 
String boatName = "shark"; 
//String boatName = "dolphin"; 

////////////////////////////////////////////////////////// set these booleans to 1 if sensor is connected, 0 if not

boolean condsensor = 1;
boolean tempsensor = 1;
boolean turbsensor = 0;
boolean pHsensor = 1;

////////////////////////////////////////////////////////////////////////////////////////////////////////////////////

// you can input: "temperature", "conductivity", "turbidity", or "pH" to get the LEDs to correspond to certain data
String whichDataControlsLEDs = "temperature";
//String whichDataControlsLEDs = "pH";
//String whichDataControlsLEDs = "conductivity";
//String whichDataControlsLEDs = "turbidity";

////////////////////////////////////////////////////////////////////////////////////////////////////////////////////

// you can input: "1.0", or "1.2" to show that the conductivity switch is using to 1.0 or the 1.2 kohm resistor
String whichResistor = "1.2";

////////////////////////////////////////////////////////////////////////////////////////////////////////////////////

//You want to choose values that are the bounds of what data you expect to see in a particular location so the color ranges well.
//Look at the data from the radio to see what values you're getting.

//SEEBOAT LED VARIABLES
int hue = 0;
uint32_t starttime; 
//temperature color range (times 10; in oF)
int lowReading1dec = 620;
int highReading1dec = 720;
//conductivity color range (in microS/cm), fresh water is ~700 microS/cm, brackish is ~50,000 microS/cm, ocean water is ~53,000 microS/cm
int lowReadingCond = 18000;
int highReadingCond = 21000;
//pH color range (unitless)
int lowReadingPH = 750; //times 100 to save decimals
int highReadingPH = 850; //times 100 to save decimals
//turbidity color range (NTU)
int lowReadingTurb = 50;
int highReadingTurb = 300; 

///////////////////////////////////////////////////////////

// this keeps track of whether we're using the interrupt
// off by default!
boolean usingInterrupt = false;
uint32_t timer = millis();

//SEEBOART SENSOR VARIABLES
const int waterPin = 2;     // the number of the pushbutton pin
// variables will change:
int waterVal = 0;         // variable for reading the pushbutton status


float tempVal;
float condVal;
uint8_t turbVal;
float pHVal;
double GPSlat;
double GPSlong;
int GPShour;
int GPSmin;
int GPSsec;
int GPSms;


//temperature variables from past code
//const int  AT30TS750_I2C =  0x48;    // I2C Address for the temperature sensor
const int  AT30TS750_I2C =  0x4B;    // I2C Address for the temperature sensor

const byte REG_TEMP      =  0x00;    // Register Address: Temperature Value
const byte REG_CONFIG    =  0x01;    // Register Address: Configuration
byte   tempLSByte       = 0;
byte   tempMSByte       = 0; 
float  floatTemperature = 0.0000;

const byte   AT30TS750_I2Cc        = 0x4B; //1001000
const byte   AT30TS750_REG_TEMP   = 0x00;  // Register Address: Temperature Value 0x00
const byte   AT30TS750_REG_CONFIG = 0x01;  // Register Address: Temperature sensor configuration
const byte   AT30TS750_REG_TEMP_RESOLUTION = 0x60; //0x00 for 9 bit; 0x60 for 12-bit
byte         timeStamp[7];                 // Byte array holding a full time stamp.
unsigned int errorCount           = 0;     // Large integer to hold a running error count
byte         errorStatus          = 0;     // Byte value to hold any returned I2C error code
byte temperature[2]; //Byte array holding the temperature; use more or less of this depending on precision.  uint_8 for whole number
//temp oC*10 for each sensor
int tempC1decA = 0;
int tempC1decB = 0;
int tempC1decC = 0;
int tempC1decD = 0;

//RADIO VARIABLES
//For radio
//Message variables
//We will save up to 10 datapoints from the past so we can average values to get light color if we want
//our message will include: deviceID, time, waterCheck, temperature, turbidity, conductivity, GPSlat, GPSlong (8 items)
const int messageLength = 8;
const int messageNum = 10;
double dataArray[messageNum][messageLength];  //two dimensional array; previously uint8_t
double tempDataArray[messageLength];    //array to hold the data while we're putting it together
uint8_t tempDataArrayInt[messageLength];  //array to hold the multiplied up integer version of the data so we can send it with less pain.
//Hold a space to put the received message values until they're stored
//uint8_t tempMessageReceive[messageLength];

//////DATA STRUCTURE
//see: http://playground.arduino.cc/Code/Struct
//also: https://stackoverflow.com/questions/13775893/converting-struct-to-byte-and-back-to-struct
//from moteino code Struct_Send
/*
typedef struct {
  int           nodeId; //store this nodeId
  unsigned long uptime; //uptime in ms
  float         temp;   //temperature maybe?
} Payload;
Payload theData;
*/

//version with the seeboat data
typedef struct {
  int boatName;
  int           deviceID; //store this nodeId
  float GPSlat; //latitude
  float GPSlong;   //longitude
  //send all the time parts individually; strings have been annoying to send
  int GPShour;
  int GPSmin;
  int GPSsec;
  int GPSms;
  float tempVal; //temperature value
  float condVal;
  float pHVal;
  float turbVal;
} Payload;
Payload theData;


/*struct dataPoint {
  byte deviceID;
  byte GPSlat;
  byte GPSlong;  
};
*/


/*
 * I have to figure out what type of array this is--has int and ? cast everything to string to send? what sends best?
  tempDataArry[1] =  GPStime;
  tempDataArry[3] =  tempVal;
  tempDataArry[4] =  condVal;
  tempDataArry[5] =  turbVal;
  tempDataArry[6] = GPSlat;
  tempDataArry[7] =  GPSlong;
*/




//also a counter to keep track of where we are in the message string
int charCounter = 0;
//and a counter to keep track of which message we're on
//the most recent message will always be stored in slot 0!! everything else gets pushed back
int messageCounter = 0;
//the number of non-99 characters in any particular message
int realMessageLength = 0;
int j = 0; //a counter that's used in the playback loops

//keep track of what mode we're in; FALSE is composing, TRUE is playback
boolean playMode = false;
//values from inside certain slots in the array
int arrayVal = 0;

//Variables for the radio sending/receiving
//variable that attaches the deviceID and the message; this is what will be sent
// for feather m0
#define RFM95_CS 8
#define RFM95_RST 4
#define RFM95_INT 3
// Change to 434.0 or other frequency, must match RX's freq!
#define RF95_FREQ 915.0
// Singleton instance of the radio driver
RH_RF95 rf95(RFM95_CS, RFM95_INT);
// Blinky on receipt
//#define LED 13
//for Tx
int16_t packetnum = 0;  // packet counter, we increment per xmission
//variable for telling us what mode we're in
//0 is Rx; 1 is Tx
int transMode = 0;

//Variable to indicate what board number this is
//This will be different for each SeeBoat!!!!!! It lets us know who the message is coming from 
const int deviceID = 444;

//pH Variables
char ph_data[20];                //we make a 20 byte character array to hold incoming data from the pH circuit.
byte in_char = 0; 
byte i = 0; 
uint32_t pH_timer = millis();
bool ask_for_data = 1;

//Conductivity Variables
int power = 5;              //50% square wave (yellow wire)Ã‚Â¯Ãƒâ€š
int sensor = A1;             //final voltage (purple wire)
float val = 0.0;

//turbidity variables
int readingMain = 10;
float MainSensor;
float microIrradiance;
float irradiance;
float kilohertz;
float milliIrradiance;

//////////////////LED Strip variables
#define DATAPIN    13
#define CLOCKPIN   11
#define NUMPIXELS 100 //can round up, the strip doesn't care if this number goes over actual # of pixels
Adafruit_DotStar strip(NUMPIXELS, DATAPIN, CLOCKPIN, DOTSTAR_BRG);

  //RGBConverter converter; //this was for a single pixel setup, don't need for strip setup
  //byte rgb[3];
//////////////////////////////////////////////////////////////////////////////////////////////////
// the setup routine runs once when you press reset:
void setup(){
  pinMode(readingMain,INPUT); //pin for turbidity

  //LED start up
  ledStartup();

  //delay(60000);
  
  //GPS start up
  GPSsetup();
  
  //radio start-up
  radioStartup();

  //Start-up the temperature sensor and the other sensors (make sure it matches the address in the function)
  sensorSetup();

  //Clear the data array
  //I need this to be a two dimensional array (matrix) now--stores the current data and x past data for averaging as needed
/*
  for (int m = 0; m < messageLength; m++) {
    tempDataArray[m] = 99;
    //tempMessageReceive[m] = 99;
  }
  for (int r = 0; r < messageNum; r++) {
    for (int k = 0; k < messageLength; k++) {
      dataArray[r][k] = 99;
    }
  }
*/
#if defined(__AVR_ATtiny85__) && (F_CPU == 16000000L)
  clock_prescale_set(clock_div_1); // Enable 16 MHz on Trinket
#endif

  starttime = millis();
  
}

//uint_8 only goes to 255
//////////////////////////////////////////////////////////////////////////////////////////////////
void loop() {
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

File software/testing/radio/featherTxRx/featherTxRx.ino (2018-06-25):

// Feather9x_RX
// -*- mode: C++ -*-
// Example sketch showing how to create a simple messaging client (receiver)
// with the RH_RF95 class. RH_RF95 class does not provide for addressing or
// reliability, so you should only use RH_RF95 if you do not need the higher
// level messaging abilities.
// It is designed to work with the other example Feather9x_TX

//Attempt by Laura to combine the Tx and Rx functionality
//The radio should have a button. Pressing that button shifts it from one mode to another

//RADIO VARIABLES
#include <SPI.h>
#include <RH_RF95.h>
/* for feather m0 */
#define RFM95_CS 8
#define RFM95_RST 4
#define RFM95_INT 3
// Change to 434.0 or other frequency, must match RX's freq!
#define RF95_FREQ 915.0
// Singleton instance of the radio driver
RH_RF95 rf95(RFM95_CS, RFM95_INT);
// Blinky on receipt
#define LED 13

//MODE BUTTON VARIABLES
const int buttonPin = 9;    // the number of the pushbutton pin
const int ledPin = 13;      // the number of the LED pin
int buttonCount = 0;  //the number of times the button presses or un-presses
float buttonPresses = 0; //the actual number of times the button has been pressed
int ledState = HIGH;         // the current state of the output pin
int buttonState;             // the current reading from the input pin
int lastButtonState = LOW;   // the previous reading from the input pin
long lastDebounceTime = 0;  // the last time the output pin was toggled
long debounceDelay = 50;    // the debounce time; increase if the output flickers

//for Tx
int16_t packetnum = 0;  // packet counter, we increment per xmission

//variable for telling us what mode we're in
//0 is Rx; 1 is Tx
int transMode = 0;

/////////////////////////////////////////////////////////////
void setup() 
{
  pinMode(buttonPin, INPUT);
  pinMode(LED, OUTPUT);     
  pinMode(RFM95_RST, OUTPUT);
  digitalWrite(RFM95_RST, HIGH);

  //take this serial line out if you're not necessarily connected to the computer!
  //while (!Serial);
  Serial.begin(9600);
  delay(100);

  Serial.println("Feather LoRa Tx-RX Test by Laura!");
  
  // manual reset
  digitalWrite(RFM95_RST, LOW);
  delay(10);
  digitalWrite(RFM95_RST, HIGH);
  delay(10);

  while (!rf95.init()) {
    Serial.println("LoRa radio init failed");
    while (1);
  }
  Serial.println("LoRa radio init OK!");

  // Defaults after init are 434.0MHz, modulation GFSK_Rb250Fd250, +13dbM
  if (!rf95.setFrequency(RF95_FREQ)) {
    Serial.println("setFrequency failed");
    while (1);
  }
  Serial.print("Set Freq to: "); Serial.println(RF95_FREQ);

  // Defaults after init are 434.0MHz, 13dBm, Bw = 125 kHz, Cr = 4/5, Sf = 128chips/symbol, CRC on

  // The default transmitter power is 13dBm, using PA_BOOST.
  // If you are using RFM95/96/97/98 modules which uses the PA_BOOST transmitter pin, then 
  // you can set transmitter powers from 5 to 23 dBm:
  rf95.setTxPower(23, false);
}


////////////////////////////////////////////////////////////////////////////////////

void loop()
{
//See what mode we're in and act accordingly
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

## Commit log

2018-06-25 major update June 2018
    [conductivity.brd, conductivity.sch, fishnet-0.5.brd, fishnet-0.5.sch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]
2018-06-25 major project update june 2018
    [fishnet-0.1.brd, fishnet-0.1.sch, riffle-CTL-0.2-blank.brd]
2018-06-25 board and parts list update june 2018
    [SeeBoat_fullPartsList.xlsx, conductivity.brd, conductivity.sch]
2018-06-26 control board update
    [controlBoard-0.5.brd, controlBoard-0.5.sch]
2018-06-27 hardware update
    [conductivity.brd, controlBoard-0.5.brd]
2018-07-24 update parts lists w/header
    [SeeBoat_fullPartsList.xlsx]
2019-03-01 Update conductivity.ino
    conductivity now outputs voltage as a float, not an int
2019-05-03 Updated main code to current LED strip + sensors.
    [SeeBoat_fullPartsList.xlsx]
2019-05-03 Revert "Updated main code to current LED strip + sensors."
    This reverts commit e346d15b47c64aa68b4e26eb6b5f228a005aae59.
    [SeeBoat_fullPartsList.xlsx]
2019-05-03 2nd try: Updated main code to current LED strip + sensors.""
2019-05-03 parts list
    [SeeBoat_fullPartsList.xlsx]
2019-05-10 Integrated all sensor code.
2019-06-12 updated parts list and adding tutorials
    [SeeBoat_fullPartsList.xlsx, conductivity.brd, conductivity.sch]
2019-06-12 parts list diode update
    [SeeBoat_fullPartsList.xlsx]
2019-06-13 parts list and boards update
    [SeeBoat_fullPartsList.xlsx, controlBoard-0.5.brd, controlBoard-0.5.sch, temperatureSensor.brd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]
2019-06-21 parts list update with new attachers and conductivity code fix
    [SeeBoat_fullPartsList.xlsx]
2019-06-21 add temperature tutorial
2019-06-26 Update Turbidity Sensor Manufacturing Tutorial .docx
2019-07-03 fixed labels on LED strand on control board, added 3D print parts
    [conductivityProbe.STL, controlBoard-0.5.brd, turbidityBoatAttachment.STL]
2019-07-03 update pH and LED testing code
2019-07-05 update conductivity headers, add 3D print parts and laser cut parts
    [SeeBoat_fullPartsList.xlsx, conductivityProbe.DXF, conductivityProbe.SLDPRT, turbidityBoatAttachment.DXF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]
2019-07-08 Made easier to change sensor variables, updated tutorials.
2019-07-09 Added control board tutorial.
2019-07-09 shorten light panels for boat, add LED holders, re-label turbidity fil
2019-07-09 add tubing conductivity holder, update boat parts
    [SeeBoat_fullPartsList.xlsx]
2019-07-11 Added LED tutorial.
2019-07-16 Added turbidity calibration tutorial, updated sensor integration tutorial, added leakTesting LED code.
2019-07-17 add LED strand fade testing code
2019-07-17 more LED code updates
2019-07-23 Updated main code to adjust calibration per boat, updated tutorials.
2019-07-30 Added pH o-rings to parts list.
    [SeeBoat_fullPartsList.xlsx]
2019-08-01 all sensor python plots, windows and linux
2019-08-02 updated sensor tutorials with wire lengths/diagrams.
    [seeBoatData_2019_08_01 10_42_17_337494.csv]
2019-08-05 Added 2nd boat calibration code.
2019-08-05 Added boatName to Rx, Tx code, updated headers in CSV code.
    [seeBoatData_2019_08_01 10_42_17_337494.csv, seeBoatData_2019_08_05 13_05_43_488103.csv]
2019-08-09 more points in python code
    [seeBoatData_2019-08-06 15:06:20.118985.csv, seeBoatData_2019-08-07 13:09:59.965530.csv, seeBoatData_2019_08_05 13_05_43_488103.csv]
2019-08-12 Zeroed conductivity so it shouldn't output any negative conductivities when the voltage = 0.
2019-08-20 deleted misc file
    [seeBoatData_2019_08_05 13_05_43_488103.csv]
2019-08-20 fixed turbidity lights code
    [seeBoatData_2019-08-06 15:06:20.118985.csv, seeBoatData_2019-08-07 13:09:59.965530.csv]
2019-08-20 fixed pH demical+LED colors
2019-08-20 Revert "fixed pH demical+LED colors"
    This reverts commit 18743cfefc8759074a153865a1ace62f1e04c31f.
2019-10-03 GPS data
    [DATALOG4.CSV]
2019-11-22 november update
    [SeeBoat_fullPartsList.xlsx, conductivity.brd, conductivity.sch, conductivityProbe.STL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]
2019-11-22 november update 2
    [seeBoatData_2019-10-16 16:10:11.788391.csv, seeBoatData_2019-10-16 16:10:55.407805.csv, seeBoatData_2019-10-16 16:12:48.954870.csv, seeBoatData_2019-10-16 16:2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]
2019-11-22 Revert "Updating."
    [SeeBoat_fullPartsList.xlsx, conductivity.brd, conductivity.sch, conductivityProbe.STL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]
2019-11-24 Unsure what these updates are.
    [SeeBoat_fullPartsList.xlsx, conductivity.brd, conductivity.sch, conductivityProbe.STL]
2019-12-13 analog decimals adding hopefully
    [seeBoatData_2019-12-06 18:07:59.032670.csv]
2019-12-13 getting rid of file
    [seeBoatData_2019-12-06 18:07:59.032670.csv]
2020-11-12 sine code nov 2020 calibration

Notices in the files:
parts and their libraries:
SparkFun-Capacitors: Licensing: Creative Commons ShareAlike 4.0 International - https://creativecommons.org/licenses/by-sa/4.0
